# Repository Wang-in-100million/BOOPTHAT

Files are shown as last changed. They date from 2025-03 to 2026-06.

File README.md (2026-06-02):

# BOOPTHAT
Files and instructions needed to build the BOOPTHAT (Batch Operating Optically Powered Targeted Heater for Activating Transgenes) setup

STEP files are currently available and f3d files will be available after they have been cleaned up slightly. Step by step instructions for assembling the micromanipulator cassettes are curretnly available.

Instructions for putting together the VFL array, assembling the entire setup, and using the probes on embryos will be uploaded eventually.

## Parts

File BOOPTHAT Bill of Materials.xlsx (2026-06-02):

BOOPTHAT Bill of Materials
Name | Link |  | Notes: The specific brands and quantities can be changed based on need and availability. The links provided are the ones that we used, with the exception of the optical fiber. We used optical fiber that we had on hand. The important specs for the optical fiber - it should be multimode (wider core, >50um), have ST connectors on both ends so that both halves can be used.
30 mW visual fault locators | https://www.amazon.com/FYBOPTWU-Visual-Locator-Singlemode-Adapter/dp/B0BXP6ZKTF | For building the setup
3D Printer Filament (PETG) Rock White | https://www.amazon.com/OVERTURE-Filament-Consumables-Dimensional-Accuracy/dp/B07PGYHYV8
Hardware - 50 M4x40, 75 M4 Hex, 25 M3x10, 25 M3 Hex | https://accu-components.com/
20 AWG wire | https://www.amazon.com/Silicone-Electrical-Conductor-Parallel-Flexible/dp/B07K9JKXM9?s=hi
T-tap wire connector | https://www.amazon.com/Brightfour-Voltage-Connectors-Stripping-24-18/dp/B0BLKBQ2JH?s=hi
10 ohm trimmer potentiometer | https://www.amazon.com/Bourns-3296Z-1-100-64Z100-Square-Potentiometer/dp/B01MZE7493
Grip Tape | https://www.amazon.com/Hampton-Adams-3-Pack-Athletic-Sports/dp/B0771MZY1J?s=industrial
Optical Fiber, ST connectors, multimode with wide core | https://www.amazon.com/FiberCablesDirect-ST-ST-Fiber-Patch-Cable/dp/B01663TVFY?s=industrial&sp_csd=d2lkZ2V0TmFtZT1zcF9hdGY
Sutter Ceramic Tile for scoring glass | https://www.autom8.com/shop/micropipette-fabrication/glass/ceramic-tile-for-cutting-glass/ | Probe cutting/coating
Acrylic primer 200mL | https://www.amazon.com/Vallejo-Black-Primer-Acry-Poly-200ml/dp/B004BMZVMK
Black 4.0 Acylic Paint 150mL | https://www.culturehustleusa.com/collections/black/products/black-4-0
Laser Power Meter, Sanwa LP10 | https://www.sanwa-america.com/products/lp10-laser-power-meter | For calibrating the setup
56 AWG thermocouple wire E,T(-) | https://www.omega.com/en-us/temperature-measurement/temperature-wire-and-cable/extension-wires-and-cables/spir/p/SPCC-0005-50
56 AWG thermocouple wire K,E(+) | https://www.omega.com/en-us/temperature-measurement/temperature-wire-and-cable/extension-wires-and-cables/spir/p/SPCH-0005-50
Thermocouple Reader | https://www.amazon.com/Fluke-Calibrated-Single-Input-Thermometer/dp/B000VRCSX4?sp_csd=d2lkZ2V0TmFtZT1zcF9hdGY (https://www.amazon.com/Proster-Thermocouple-Thermometer-Dual-Channel-Thermocouples/dp/B071V7T6TZ)
E-type thermocouple connector | https://www.amazon.com/MECCANIXITY-Thermocouple-Connectors-Adapter-Temperature/dp/B0C348T7KD

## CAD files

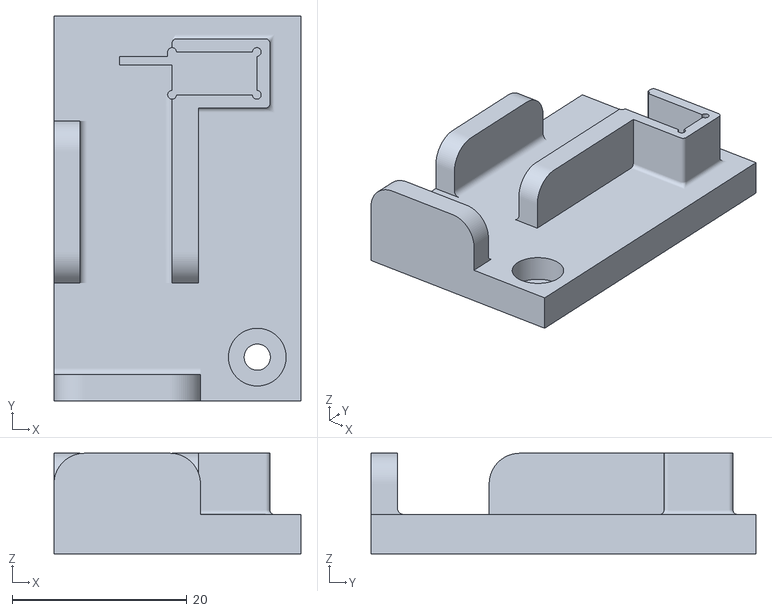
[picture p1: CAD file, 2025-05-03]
Micromanipulator Cassette STEP files/Insert.stl
28.2 x 44.0 x 11.5

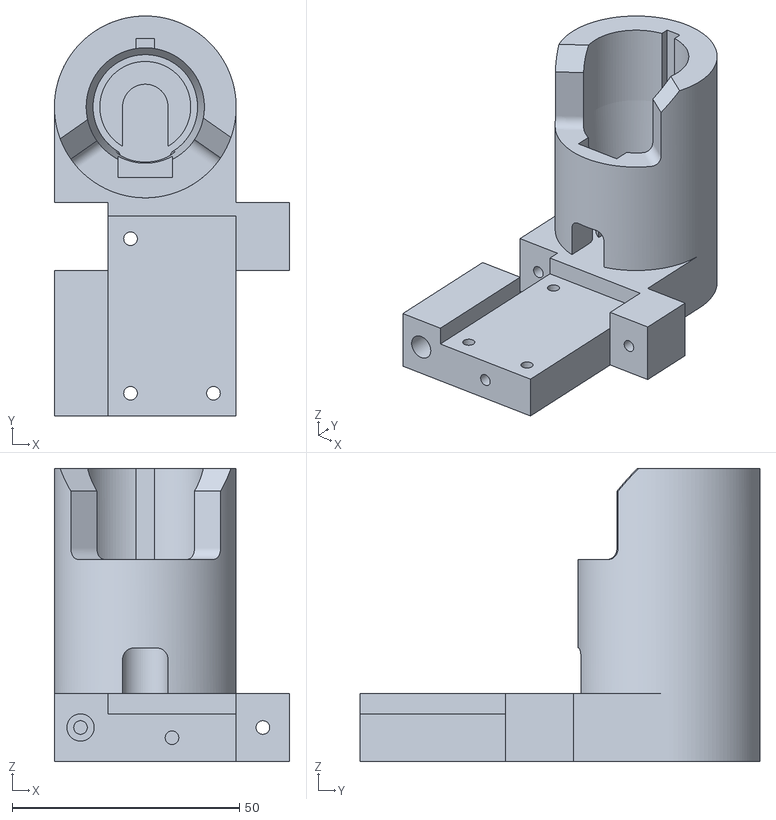
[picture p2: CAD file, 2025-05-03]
VFL_holder/ModularVFLMiddle.stl
51.8 x 88.0 x 64.5

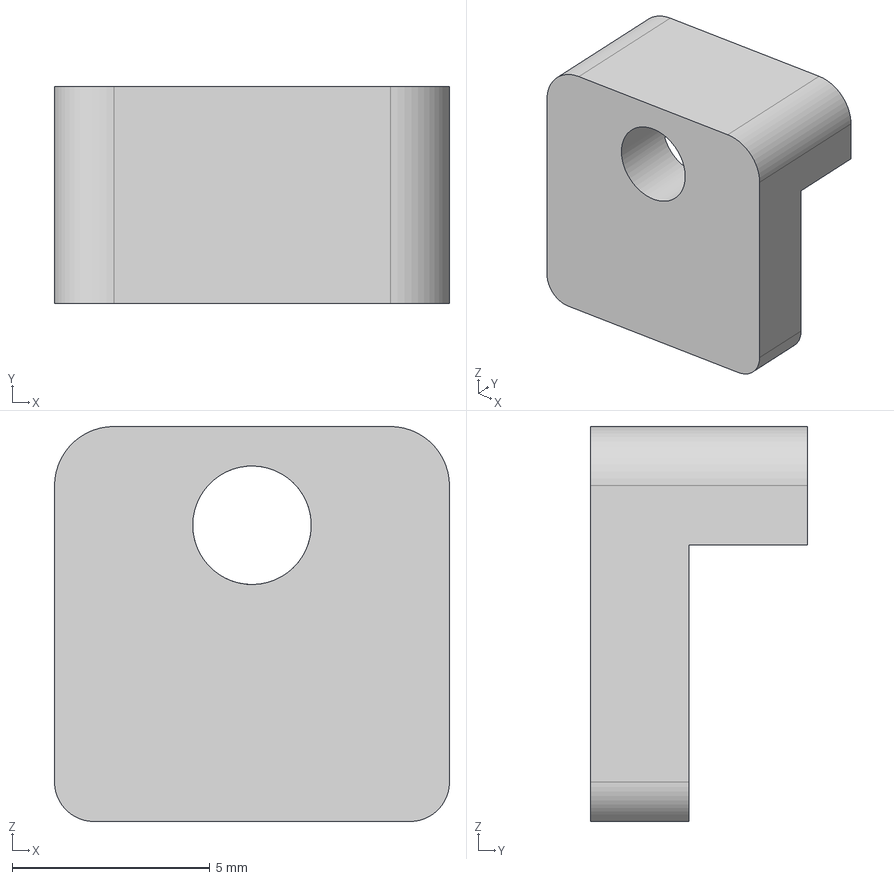
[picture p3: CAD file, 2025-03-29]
Micromanipulator Cassette STEP files/Fiber Clamp.step
10.0 x 5.50 x 10.0 mm

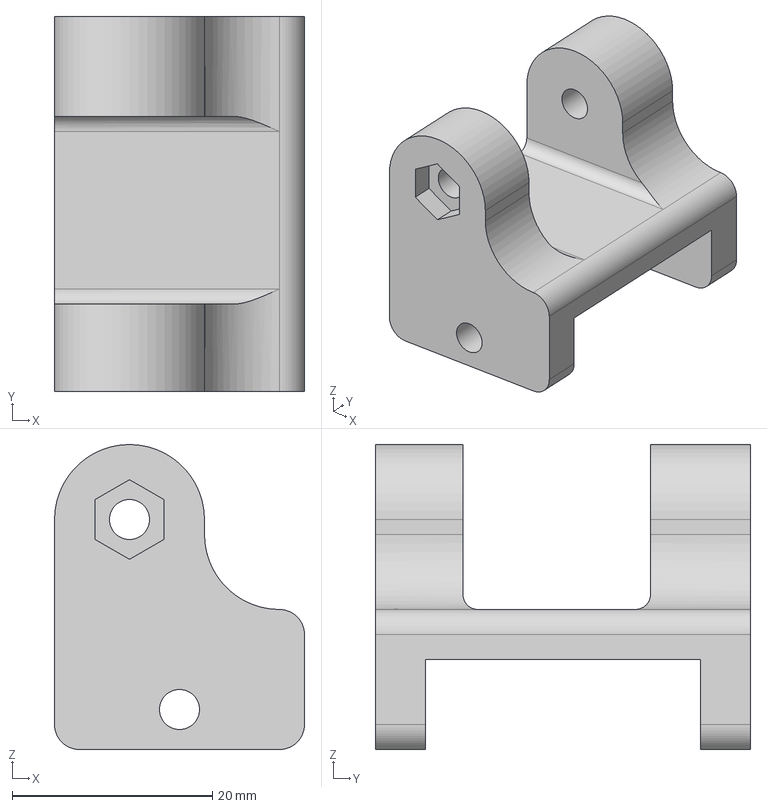
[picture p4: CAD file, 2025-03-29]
Micromanipulator Cassette STEP files/Y-axis Rail.step
25.0 x 37.5 x 30.5 mm

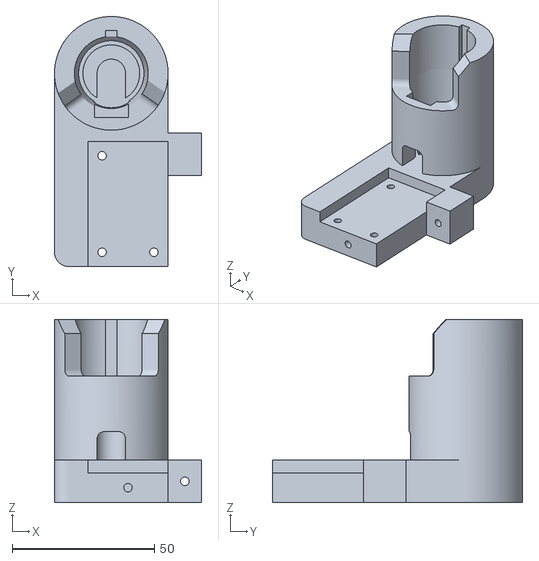
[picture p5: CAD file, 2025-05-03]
VFL_holder/ModularVFLLeft.stl
51.8 x 88.0 x 64.5

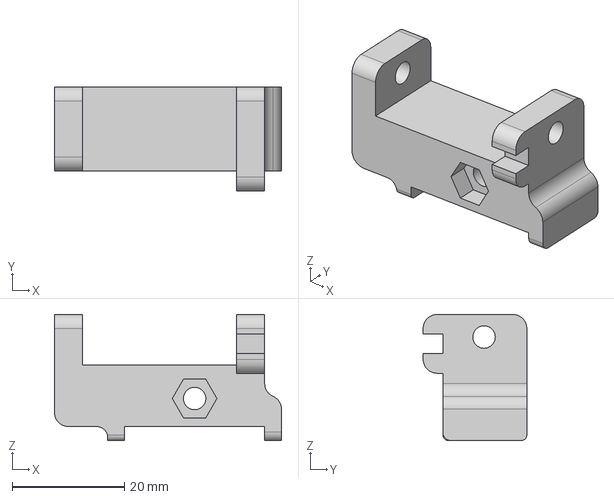
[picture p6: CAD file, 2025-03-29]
Micromanipulator Cassette STEP files/Z-axis rail and Y-axis carriage.step
40.5 x 18.5 x 22.5 mm

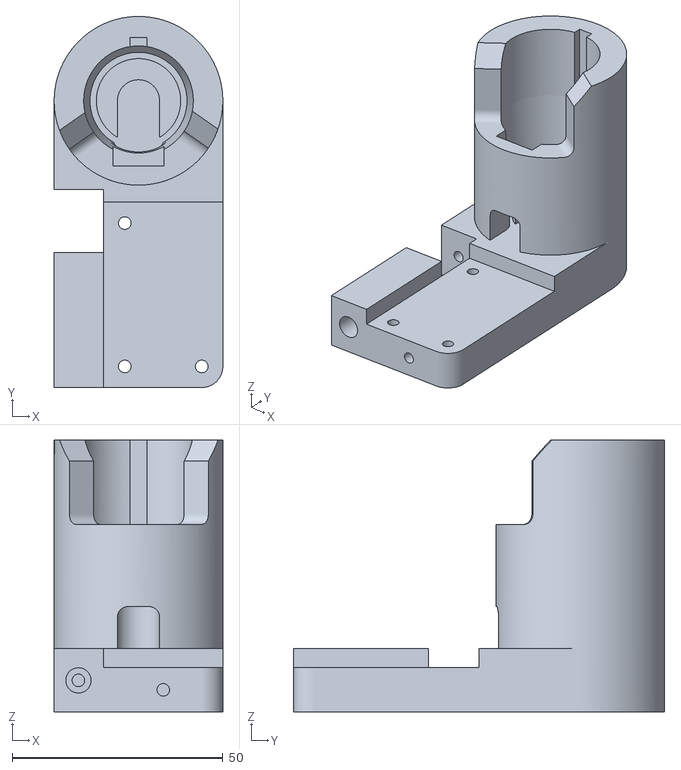
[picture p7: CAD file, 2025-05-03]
VFL_holder/ModularVFLRight.stl
40.0 x 88.0 x 64.5

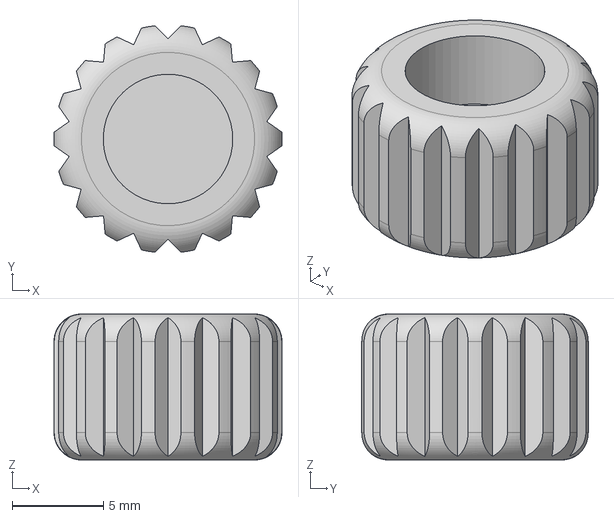
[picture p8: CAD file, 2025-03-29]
Micromanipulator Cassette STEP files/M4 Knob.step
12.5 x 12.4 x 8.00 mm

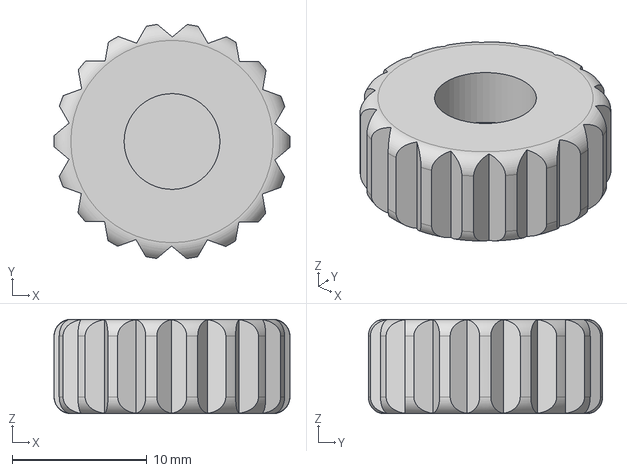
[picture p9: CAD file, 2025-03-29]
Micromanipulator Cassette STEP files/M4 Knob Large.step
17.5 x 17.4 x 7.00 mm

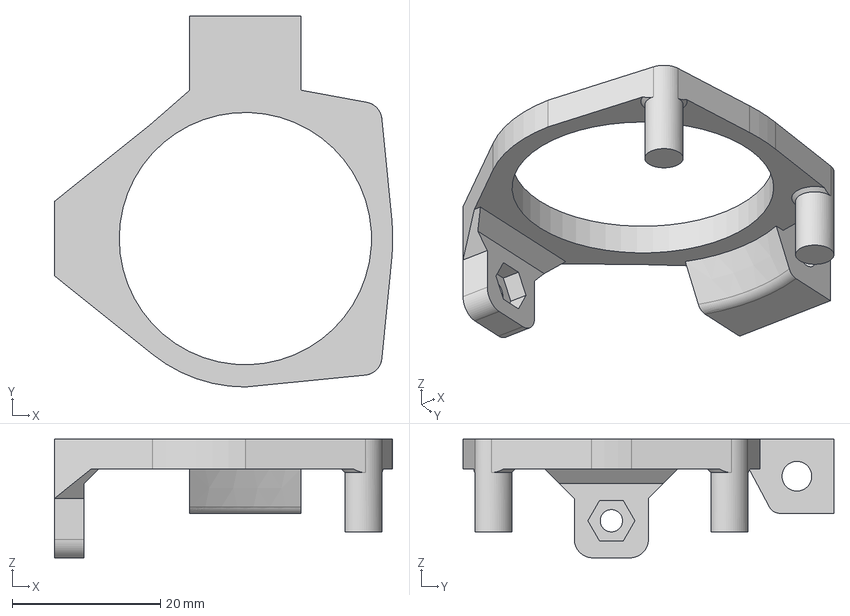
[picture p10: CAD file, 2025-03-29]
Micromanipulator Cassette STEP files/Petri Dish Holder.step
45.6 x 50.0 x 16.0 mm

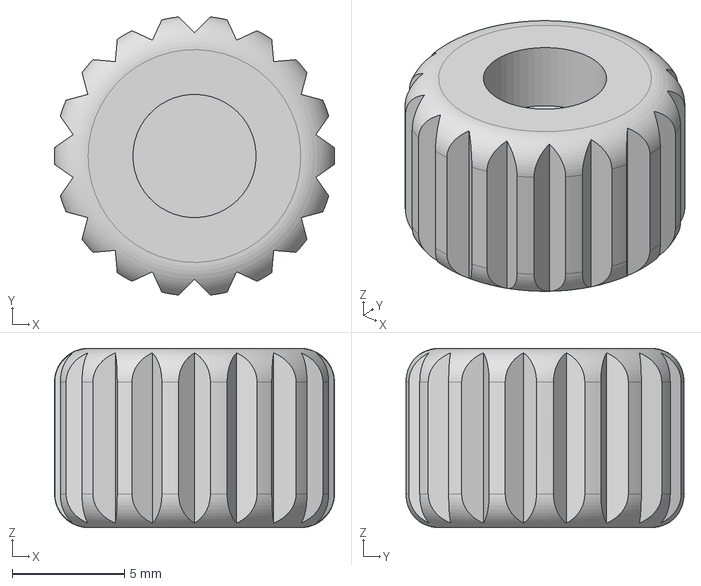
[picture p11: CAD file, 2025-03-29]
Micromanipulator Cassette STEP files/M3 Knob.step
12.5 x 12.4 x 8.00 mm

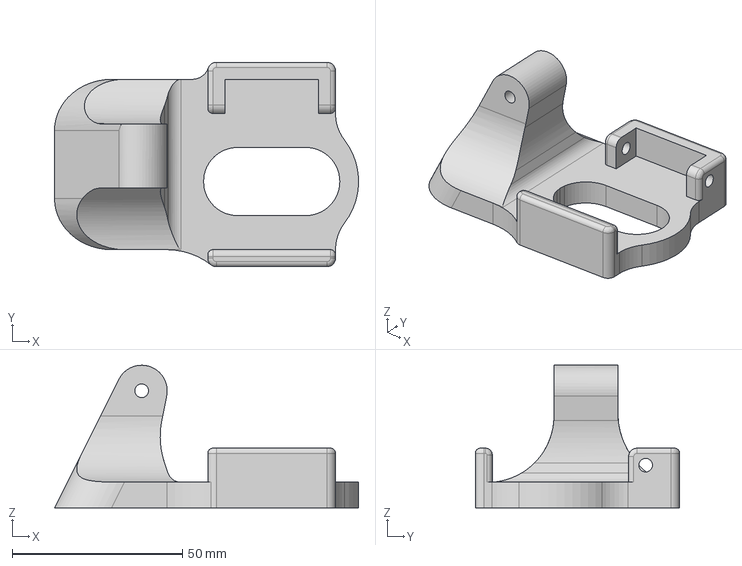
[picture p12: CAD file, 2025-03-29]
Micromanipulator Cassette STEP files/Base.step
89.2 x 60.0 x 41.8 mm

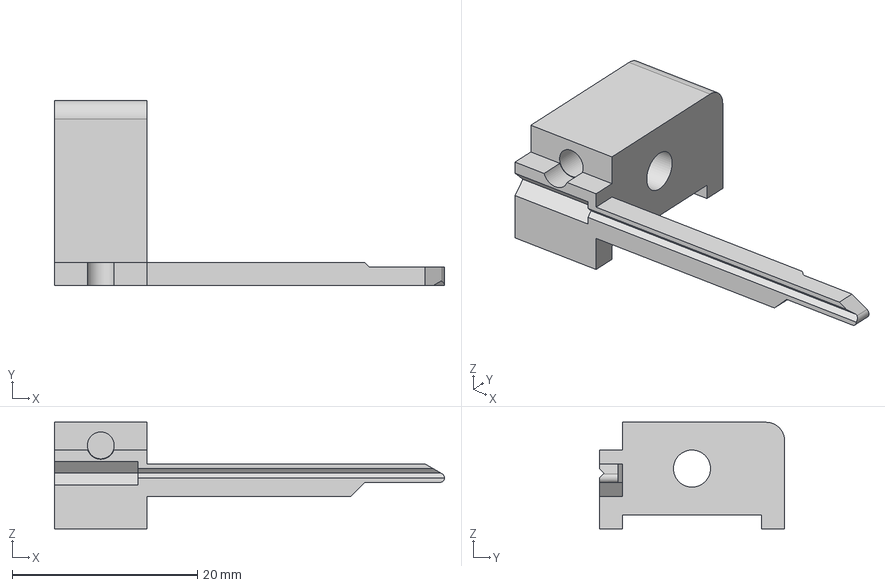
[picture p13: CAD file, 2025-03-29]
Micromanipulator Cassette STEP files/ Fiber Shuttle.step
42.1 x 20.0 x 11.5 mm

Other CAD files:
VFL_holder/Insert Right.stl
Micromanipulator Cassette Mk5.f3z
Modular VFL Holder.f3d

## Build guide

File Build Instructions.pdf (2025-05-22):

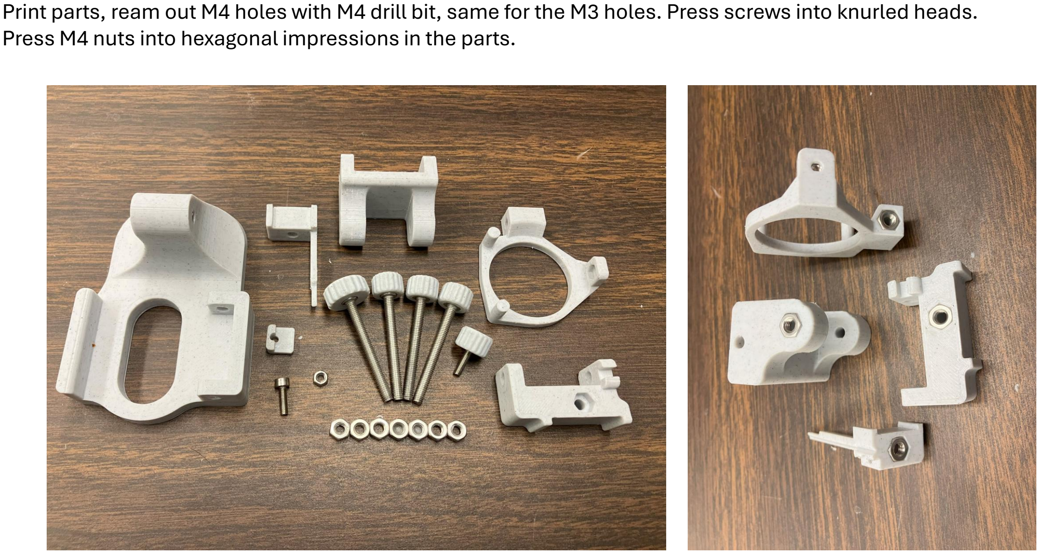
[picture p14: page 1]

Print parts, ream out M4 holes with M4 drill bit, same for the M3 holes. Press screws into knurled heads. Press M4 nuts into hexagonal impressions in the parts.

Press M3 nut into the petri dish holder, attach petri dish holder to base. Glue nut to the end of screw to hold in place. Sand and use grease to ensure smooth movement.

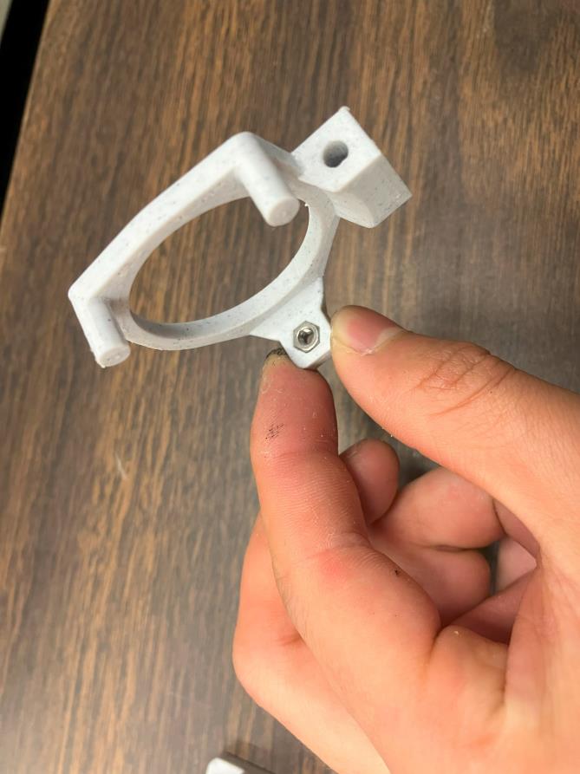
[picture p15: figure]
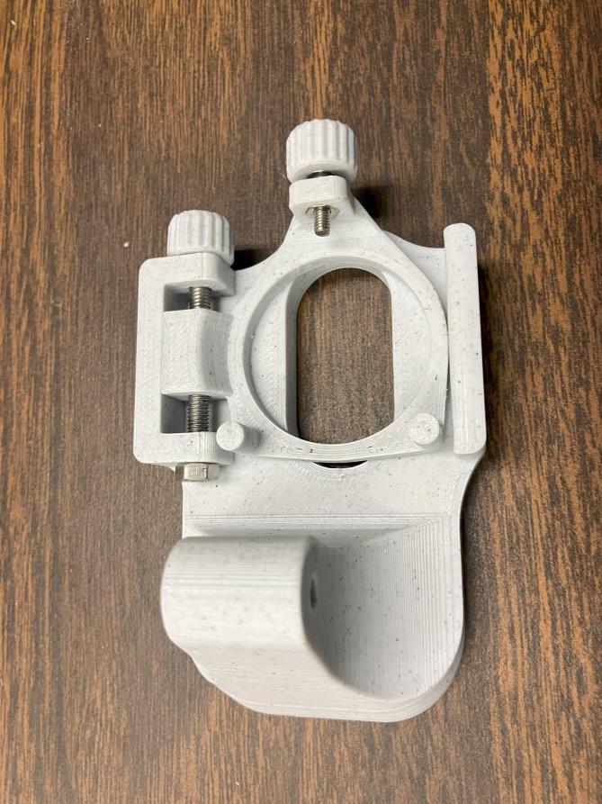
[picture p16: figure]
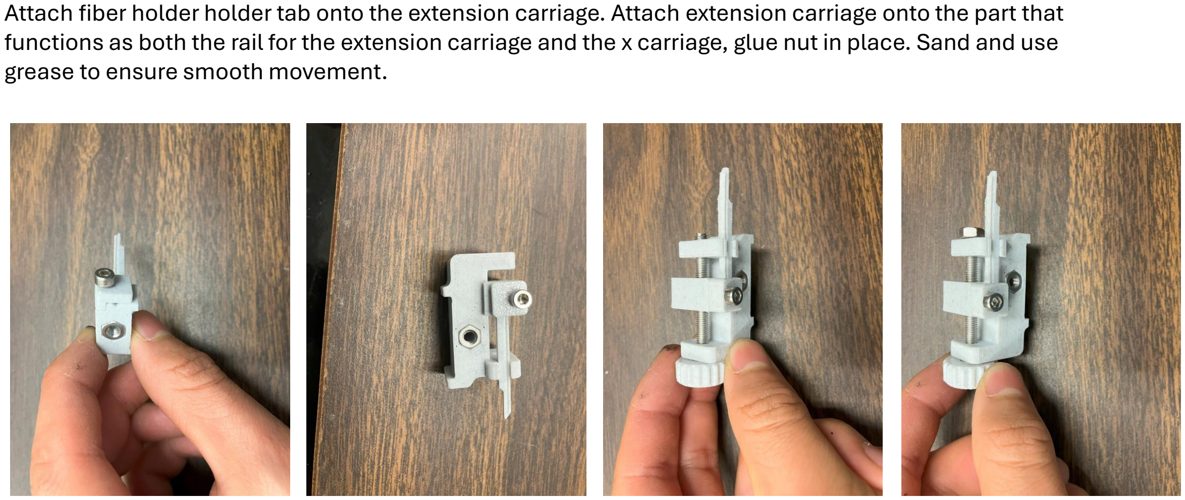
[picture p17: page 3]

Attach fiber holder holder tab onto the extension carriage. Attach extension carriage onto the part that functions as both the rail for the extension carriage and the x carriage, glue nut in place. Sand and use grease to ensure smooth movement.

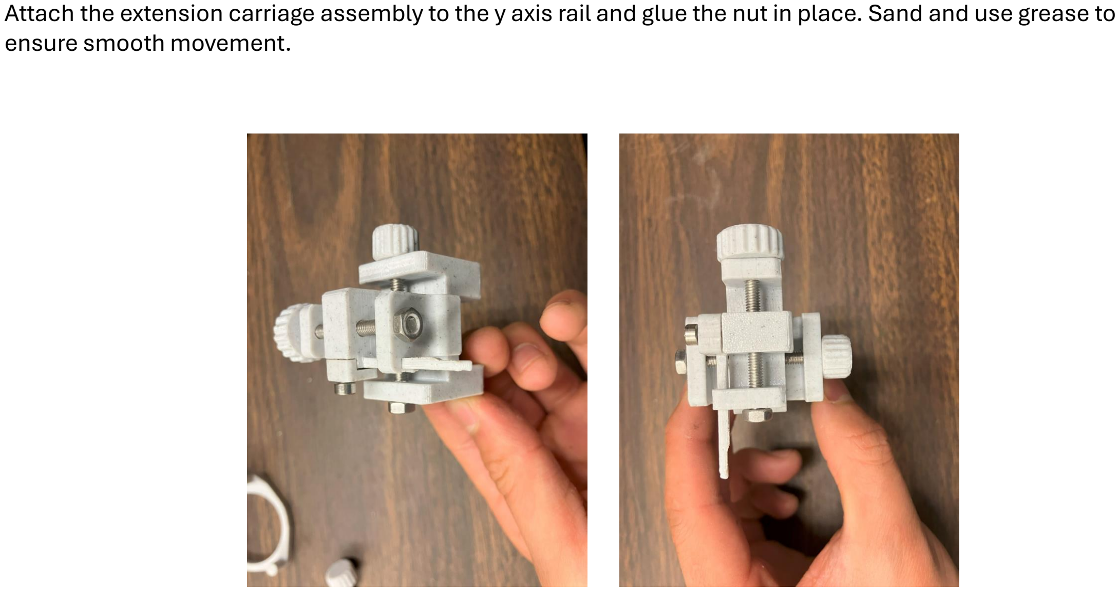
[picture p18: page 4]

Attach the extension carriage assembly to the y axis rail and glue the nut in place. Sand and use grease to ensure smooth movement.

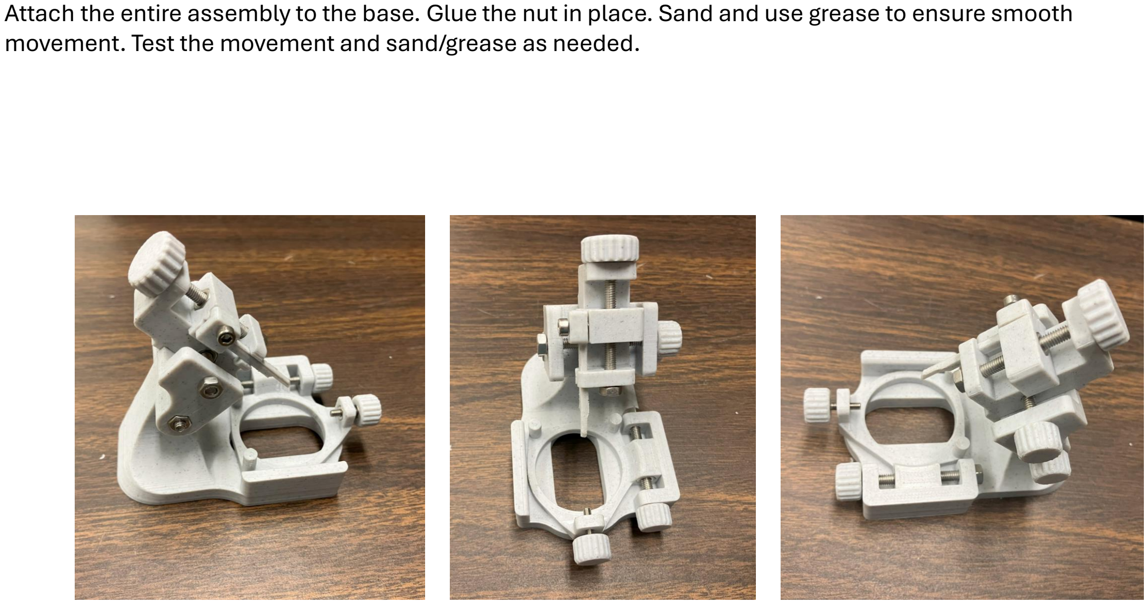
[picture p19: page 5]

Attach the entire assembly to the base. Glue the nut in place. Sand and use grease to ensure smooth movement. Test the movement and sand/grease as needed.

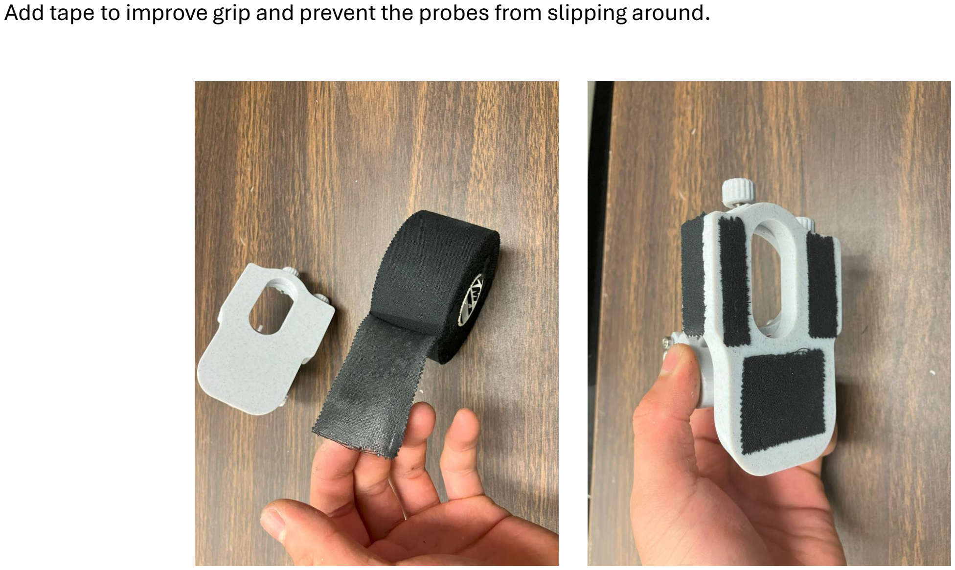
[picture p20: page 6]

Add tape to improve grip and prevent the probes from slipping around.

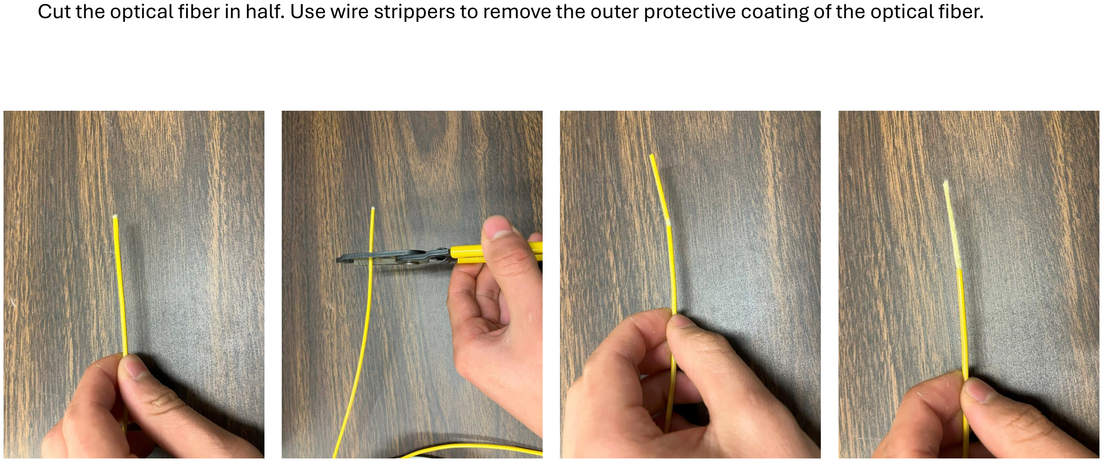
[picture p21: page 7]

Cut the optical fiber in half. Use wire strippers to remove the outer protective coating of the optical fiber.

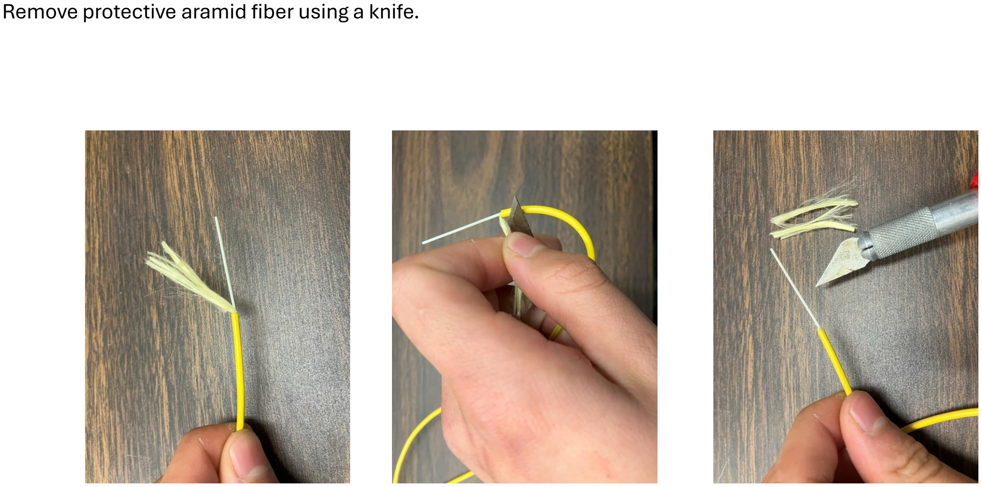
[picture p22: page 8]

Remove protective aramid fiber using a knife.

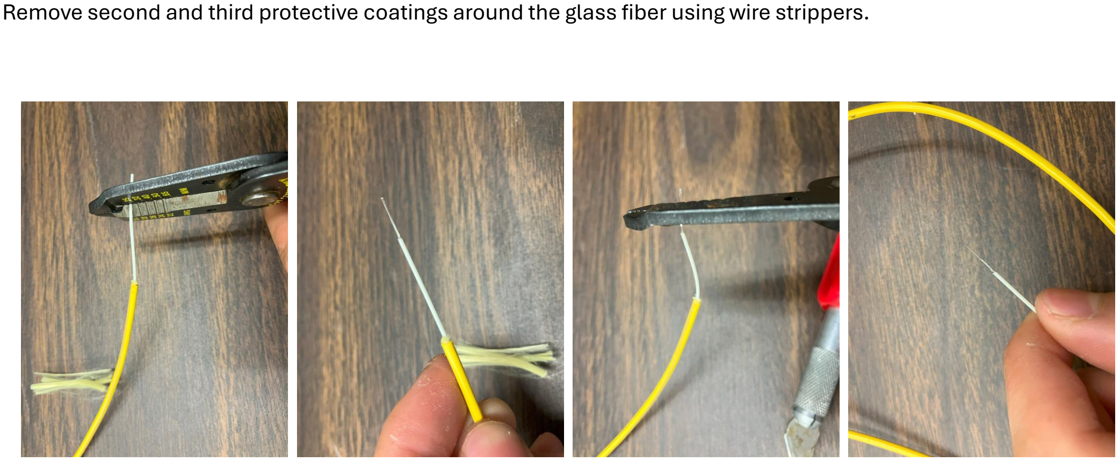
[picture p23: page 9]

Remove second and third protective coatings around the glass fiber using wire strippers.

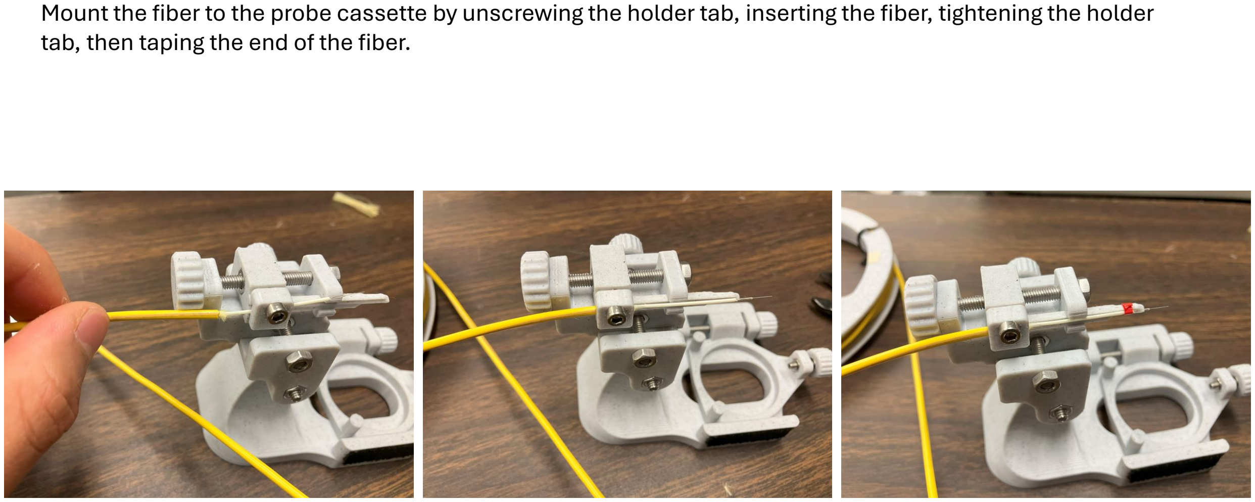
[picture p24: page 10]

Mount the fiber to the probe cassette by unscrewing the holder tab, inserting the fiber, tightening the holder tab, then taping the end of the fiber.

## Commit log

2025-03-29 Update and rename Base.step to Micromanipulator Cassette STEP files/Base.step
    [Base.step]
2025-03-29 Update and rename Fiber Clamp.step to Micromanipulator Cassette STEP files/Fiber Clamp.step
    [Fiber Clamp.step]
2025-03-29 Update and rename Fiber Shuttle.step to Micromanipulator Cassette STEP files/ Fiber Shuttle.step
    [Fiber Shuttle.step]
2025-03-29 Update and rename M3 Knob.step to Micromanipulator Cassette STEP files/M3 Knob.step
    [M3 Knob.step]
2025-03-29 Update and rename M4 Knob Large.step to Micromanipulator Cassette STEP files/M4 Knob Large.step
    [M4 Knob Large.step]
2025-03-29 Update and rename M4 Knob.step to Micromanipulator Cassette STEP files/M4 Knob.step
    [M4 Knob.step]
2025-03-29 Update and rename Petri Holder.step to Micromanipulator Cassette STEP files/Petri Dish Holder.step
    [Petri Dish Holder.step]
2025-03-29 Update and rename Y-axis Rail.step to Micromanipulator Cassette STEP files/Y-axis Rail.step
    [Y-axis Rail.step]
2025-03-29 Update and rename Z-axis rail and Y-axis carriage.step to Micromanipulator Cassette STEP files/Z-axis rail and Y-axis carriage.step
    [Z-axis rail and Y-axis carriage.step]
2025-05-03 Rename Insert Right.stl to VFL_holder/Insert Right.stl
    [Insert Right.stl]
2026-06-02 Rename Insert.stl to Micromanipulator Cassette STEP files/Insert.stl
    [Insert.stl]
